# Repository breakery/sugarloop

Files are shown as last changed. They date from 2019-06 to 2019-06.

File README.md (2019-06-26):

# Sugarloop
A waterproof case with inductive charging for RileyLink boards (433 & 915 MHz versions)
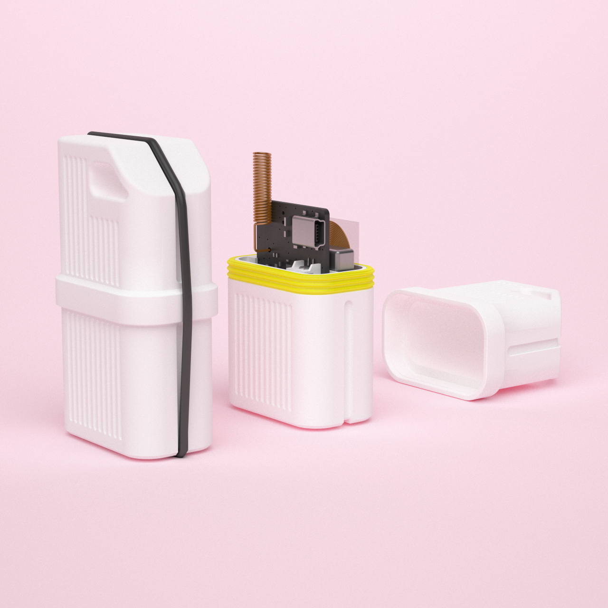
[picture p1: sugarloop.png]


## Case
The waterproof case consists of two parts (top and bottom), is sealed by a silicone seal and held in place by a rubber band. Feel free to print one yourself or have a look at Shapeways if you do not have access to a 3D printer.

### Print settings
Some very decent print result was archieved with the following setup:
- Prusa i3 MK2
- 0.4mm extruder nozzle
- Infill 20%
- High quality PLA, preferable white color to better see the charging LED
- Support structure for top of the case with some additional support blockers
- print time for top and bottom about 4 hours

### Seal
The main silicone seal is borrowed from AMP Superseal connector with 6 positions ([Digikey Partnumber A106530-ND](https://www.digikey.com/products/en?keywords=A106530-ND)). Any rubber band with decent tension is good enough to hold to top and bottom of the case in place.

## Hardware

### Inductive charging module
To add reliable inductive charging to the case make sure to use [Adafruits Universal Qi Wireless Receiver Module](https://www.adafruit.com/product/1901). The flex PCB might be cut off (1mm) on the left side in oder to fit the top-case. Connect the charging module to 'ALT PWR' on RileyLink side. Make sure to double check for ground and VCC. Any (cheap) QI certified charging basestation works fine to charge the battery. The red charging LED will turn off when the battery is fully charged. 

### Battery
The battery compartment can hold up to a 900mAh LiPo battery pack with a standard JST-PH connector (2mm pitch). Make sure there is enough space between the inductive charging module and the LiPo battery due to expansion while charging. Sucessfully tested with a LiPo battery 42mm x 34mm x 6mm.

## Test before use
Please make sure to test your case in a water condition before inserting the electronic components. Small pieces of paper added to the case compartments work fine to detect potential water leaks.

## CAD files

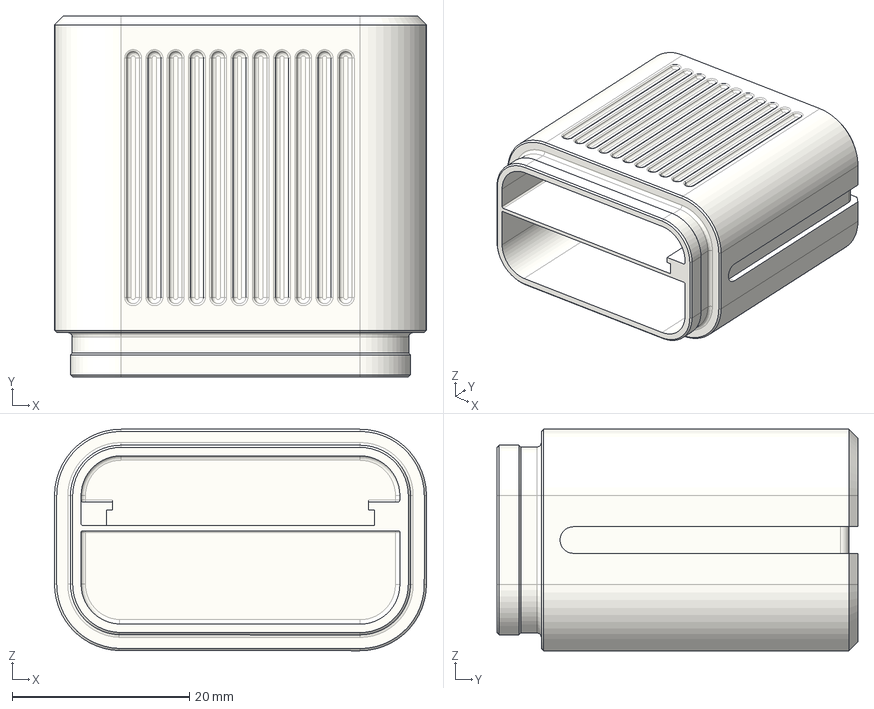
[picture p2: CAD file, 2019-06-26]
case/step/sugarloop_case_bottom.step
42.0 x 40.8 x 25.0 mm

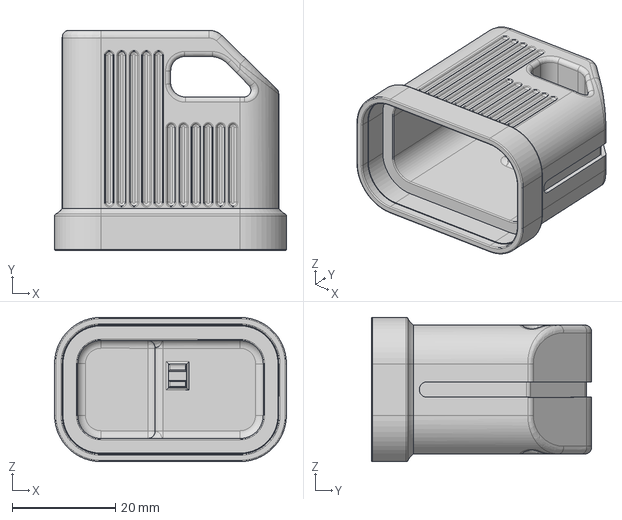
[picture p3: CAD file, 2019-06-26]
case/step/sugarloop_case_top.step
45.0 x 42.8 x 28.0 mm
